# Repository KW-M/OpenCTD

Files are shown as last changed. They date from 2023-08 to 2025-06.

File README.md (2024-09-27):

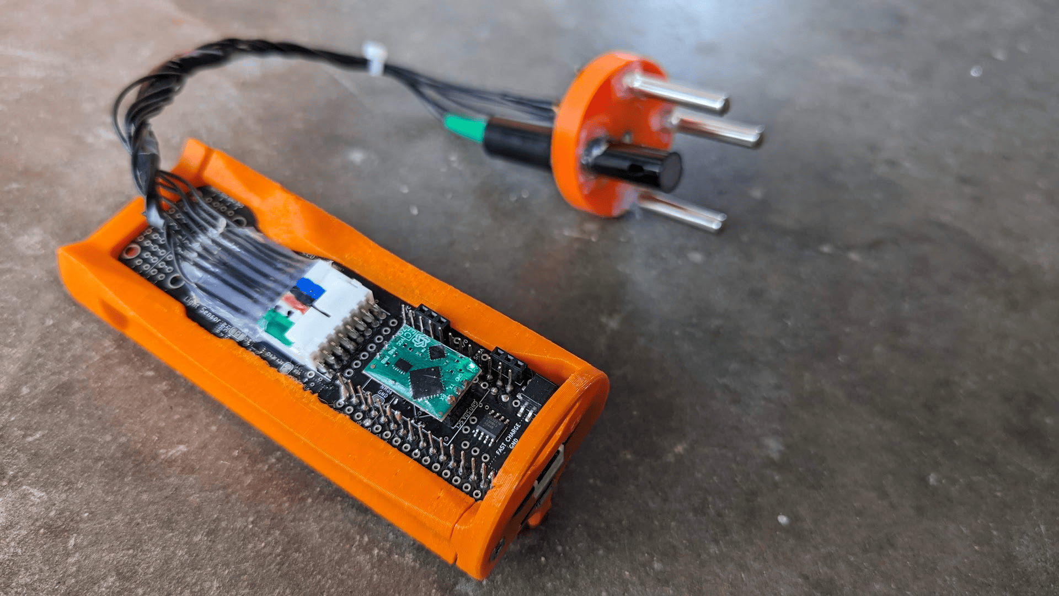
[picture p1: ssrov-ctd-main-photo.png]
SSROV CTD Header Photo


# OpenCTD SSROV / Education Edition!

This fork contains a modified version of the [OpenCTD](https://github.com/OceanographyforEveryone/OpenCTD) designed to be more reliable, easy to use, and useful as a hands-on classroom teaching tool - Developed for the [SSROV Summer Camp](https://ssrovcamp.org/) - Funding provided by the camp and the National Science Foundation

**Improvements**

- Much more reliable magnetic switch - hold to power on/off - works while fully sealed!
- Data download, calibration & configuration over USB - removes the need to take anything out of the tube or change firmware for use & calibration.
- Supports realtime plotting of sensors via the Arduino serial plotter.
- Configurable sample rate for fast response or extended battery life.
- Bright status LEDs that work in sunlight
- Includes proto space for extending with your own sensors or components.
- Built in slots for ambient lux and 9-axis orientation sensors.
- Connectors make major conmponents, mainboard and tube easily replaceable.
- Factory assembly PCB design - less soldering required and better components for very resonable prices via JLCPCB (30$ + shipping for 5 assembled boards).

**There are many other great open source CTDs used for different applications**

CTDizzle: https://github.com/IanTBlack/CTDizzle

Arduino-based Sonde: https://github.com/glockridge/DrifterApplication

OpenCTD: https://github.com/OceanographyforEveryone/OpenCTD

PiCTD: https://github.com/haanhouse/pictd

## Make your own

> Build and ordering guides comming soon

All things related to the SSROV OpenCTD are found in the [SSROV CTD](./SSROV%20CTD/) folder including:

- [Source code](./SSROV%20CTD/Software/Firmware/ssrov_ctd_code) in Arduino c++ and [pre-compiled binaries](./SSROV%20CTD/Software/Firmware/ssrov_ctd_code/build) for the Adafruit Feather Adalogger - M0 microcontroller.
- [PCB designs](./SSROV%20CTD/Hardware/Electronics/PCB/ssrov-kicad-openctd) in KiCad and exported [pcb trace & assembly files](./SSROV%20CTD/Hardware/Electronics/PCB/ssrov-kicad-openctd/production/) for ordering assembled circuit boards from JLCPCB.
- [3D Printer files](./SSROV%20CTD/Hardware/3D-Prints) and [CAD Designs](https://cad.onshape.com/documents/1210ba157fe929ee8ac86200/w/c68b7dc340291ef5042e473d/e/f126e805a19383355f9e1651) for Onshape.

Submit a github issue and let us know if you want make one or modify for your usecase! - We are happy to help!

### Development Notes:

> Please be advised that the rubber o-rings in the yellow Cherne brand endcaps is much stiffer than the rubber used in other endcap brands and has been found to fail consistently in cold water. We do not recommend using Cherne endcaps in your CTD build.
>
> Some batteries ordered from Amazon have the positive and negative termninal reversed. Please check battery polarity before attempting to power your CTD.

# OpenCTD: Oceanography for Everyone

**BELOW IS THE README FROM THE ORIGNAL OPENCTD PROJECT**

- Directions here do not nessisarily apply to ssrov CTD.

The [OpenCTD Construction and
Operation](https://github.com/OceanographyforEveryone/OpenCTD/tree/main/Documentation/Manual)
manual provides a comprehensive, step-by-step guide to building your own
OpenCTD, with a standard construction pathway as well as numerous alternatives
depending on parts availability and technical skills.

The OpenCTD [core software](https://github.com/OceanographyforEveryone/OpenCTD/tree/main/Software) is designed
to be used with an M0-style Arduino microcontroller, for which we recommend the
[Adafruit Adalogger Feather M0](https://www.adafruit.com/product/2796).

---

There is something radical about making and using your own scientific
instruments. The structure of scientific inquiry has coalesced around a model
that is, in general, both expensive and exclusive. This centralizes knowledge
production within a small circle of individuals, organizations, and
institutions who have access to substantial financial resources. This circle
rarely reflects the breadth of identities, experiences, and ways of knowing
that are most directly connected to the places being explored.

By building your own instruments to study and understand the natural world, you
are expanding the circle of knowledge production. A scientist who can make
their own instruments is not beholden to the cycles of funding and access that
constrain formal, institutional inquiry. A researcher who can build and repair
their own equipment is not dependent on the whims of academic sentiment to
decide what is and is not worthy of study. A community leader who has the tools
to create their own data does not have to wait for institutions to take notice
of an emerging crisis before taking action.

The OpenCTD

**You don’t need to ask for permission to understand your world.**

Nowhere is this inequality of access more pronounced than in the ocean
sciences, where all but a few entities have the capital to mount major
oceanographic research campaigns. Even localized coastal research can be
thwarted by lack of access to vessels, equipment, and instruments. As the need
to understand the dramatic changes at the surface and beneath the waves
accelerates, baring the participation of ocean stakeholders erodes our
power to understand, anticipate, and mitigate those changes.

The ocean belongs to everyone. The tools to study the ocean should be
accessible to anyone with the curiosity and motivation to pursue that inquiry.
Chief among these tools is the workhorse of oceanography, the CTD, an
instrument that measures salinity, temperature, and depth. By these
characteristics, scientists can begin to unlock ocean patterns hidden beneath
the sea's surface.

CTDs come in a variety of shapes, sizes, and applications. Most oceanographic
research vessels have a CTD connected to a rosette platform, which houses other
instruments and collects water samples in parallel with real-time data. CTDs
are also commonly attached to fixed moorings, autonomous underwater vehicles
(AUVs), remote-operated vehicles (ROVs), and even to marine animals.

Unfortunately, commercial CTDs are expensive. The most affordable models cost
several thousand dollars. For near-shore oceanographic research on the
relatively shallow continental shelf, this cost can be prohibitive. This
effectively excludes formal researchers from low and middle income countries,
and small island states. Even in high-income countries, formal researchers at
teaching institutions or at early career stages may also find themselves priced
out of ocean research. Informal researchers such as citizen oceanographers,
educators, conservation and management practitioners and students of all levels
face severe challenges accessing expensive scientific instruments.

### Build Your Own CTD

The OpenCTD is a low-cost, open-source CTD designed for budget-restricted
scientists, educators, and researchers working in nearshore coastal ecosystems.
In these waterways, entire research projects can be conducted for less than the
cost of a commercial CTD. OpenCTD was developed by a core team of marine
ecologists in collaboration with a community of scientists, engineers, makers,
and conservation practitioners from around the world. It is assembled from
components commonly available at large hardware stores or through major online
retailers. An Arduino-based microcontroller controls an array of sensors sealed
within a PVC pipe. Power is provided by a standard 3.7V lithium polymer battery
and data are stored in a tab-delimited text file accessed via SD card. All
OpenCTD software is released open source with no restrictions on use.

The OpenCTD is designed to be built by the end-user, providing both access to
the tools of oceanography as well as the skills to maintain, repair, and
replace OpenCTDs. For scientists working in remote settings, the repairability
of the OpenCTD is intended to prevent equipment failures from spiraling into
project failures. For educators seeking novel, in-depth, hands-on STEM
experience for advanced students, the process of building an OpenCTD offers an
introduction to coding, 3D-printing, hardware prototyping, and electronics.
Construction of an OpenCTD can provide a practical foundation for courses in
oceanography and marine or environmental science.

### Core Resources

The [OpenCTD Construction and
Operation](https://github.com/OceanographyforEveryone/OpenCTD/tree/main/Documentation/Manual)
manual provides a comprehensive, step-by-step guide to building your own
OpenCTD, with a standard construction pathway as well as numerous alternatives
depending on parts availability and technical skills. A shorter manual covering just the calibration process is also available.

The OpenCTD [core software](https://github.com/OceanographyforEveryone/OpenCTD/tree/main/Software) is designed
to be used with an M0-style Arduino microcontroller, for which we recommend the
[Adafruit Adalogger Feather M0](https://www.adafruit.com/product/2796).

You can find all the Arduino libraries as described in the manual, as well as
software for calibrating the conductivity sensors in
[Support](https://github.com/OceanographyforEveryone/OpenCTD/tree/main/Software/Support).

Hardware file for both 3D printable components and the control unit PBC can be found in [Hardware](https://github.com/OceanographyforEveryone/OpenCTD/tree/main/Hardware)

**Updated 8/27/2024**

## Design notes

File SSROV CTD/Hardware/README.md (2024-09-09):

# OpenCTD Hardware

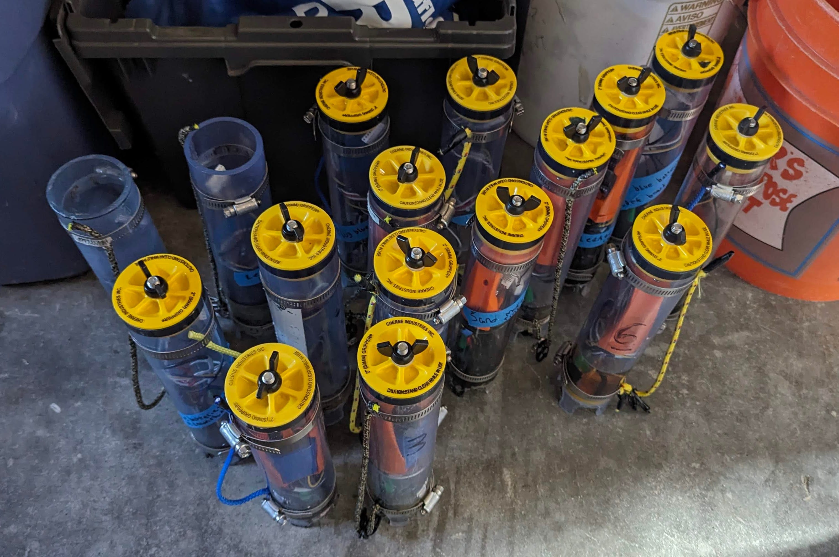
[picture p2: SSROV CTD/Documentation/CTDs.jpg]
SSROV CTDs Assembled

This directory contains files for building the OpenCTD. There are two general systems here:

- The "main board" electronics assembly including microcontroller, sd card, sensor interfaces, power controls, 3D printed internal frame, etc...
- The enclosure, which includes both the clear PVC tube + 3D printed
  base needed to construct the waterproof housing and the epoxied sensors + wires + connector that makes the OpenCTD an oceanographic instrument.

### Electronics

Electronics with tube components attached
The SSROV OpenCTD is controlled by an [Adalogger Feather
M0](https://www.adafruit.com/product/2796) microcontroller development board.
Instructions on how to upload OpenCTD firmware to the microcontroller board can
be found in the [Documentation](../Documentation). General instructions and
learning resources about the Adalogger Feather M0 board itself can be found in
the [Adafruit Learning
Guide](https://learn.adafruit.com/adafruit-feather-m0-adalogger/).

The SSROV OpenCTD mainboard is made from a largely pre-assembled custom pcb. The custom PCB is designed using [KiCad](https://www.kicad.org/), and can
be ordered in small batches from JLCPCB
using the files located in the [PCB](Electronics/PCB) directory.

### Enclosure

Most of the OpenCTD enclosure is constructed from PCV tubing and plumbing components. The base should be 3d printed and permanently epoxied along with the sensors for pressure, temprerature and salinity into the enclosure tube.

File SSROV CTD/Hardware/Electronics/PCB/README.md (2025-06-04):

# OpenCTD SSROV PCB

The OpenCTD main board is designed using [KiCad](https://www.kicad.org/) and made to be fabricated and assembled using JLCPCB.

prebuilt gerber and assembly files can be found in [./ssrov-kicad-openctd/production/](./ssrov-kicad-openctd/production/)
video guide on ordering will be shared soon

Factory Assembled main board:
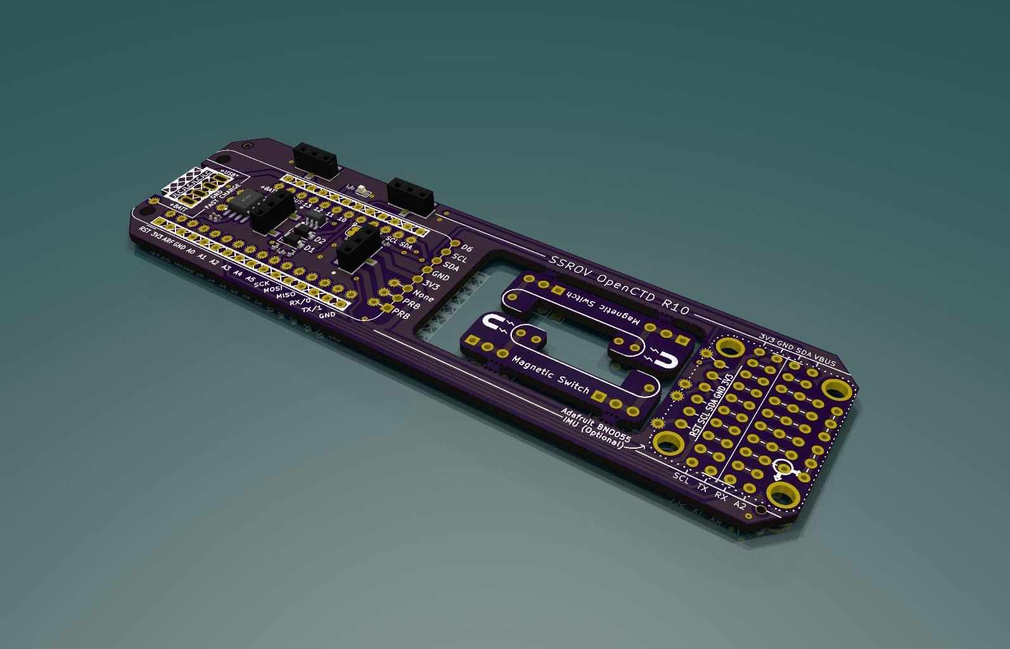
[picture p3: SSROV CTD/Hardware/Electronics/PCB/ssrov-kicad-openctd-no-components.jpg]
Factory Assembled PCB


Main board after manual assembly including optional components:
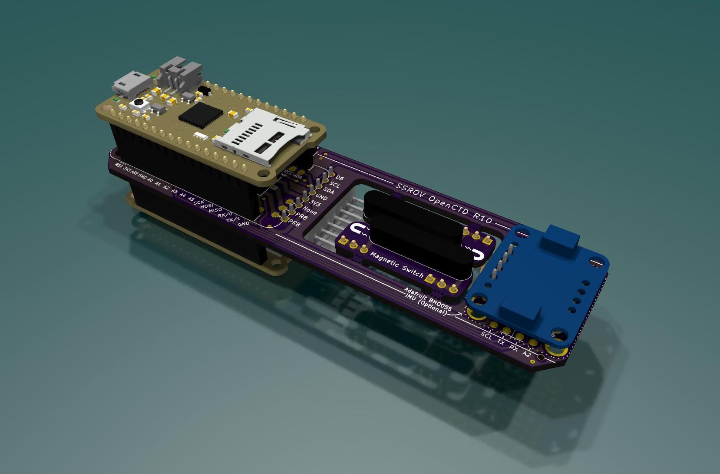
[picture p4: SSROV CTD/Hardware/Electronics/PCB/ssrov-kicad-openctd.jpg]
finished PCB after manual assembly


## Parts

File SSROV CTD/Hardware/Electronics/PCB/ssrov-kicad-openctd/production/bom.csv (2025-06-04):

Designator | Footprint | Quantity | Value | LCSC Part #
C1, C7 | 0402 | 2 | 100nF | C1525
C2, C8 | 0402 | 2 | 10uF | C15525
D1, D2 | D_SOD-123 | 2 | 1N4148W | C81598
D6-R4 | 0402 | 1 | 4.7k | C25900
EC_CONN_A1, EC_CONN_B5, REED_SWITCH_CONN1, REED_SWITCH_CONN2 | HDR-SMD_3P-P2.54-V-M-LS4.8_R1 | 4 | Conn_01x03_Female | C42379196
LED-R3 | 0402 | 1 | 470Ω | C25117
LED_D3 | 0603 | 1 | WHITE LED | C2290
NOT-NOT-GATE1 | SOT-23-6_L2.9-W1.6-P0.95-LS2.8-BL | 1 | SN74LVC2G14DBVR | C12401
PWR-R1, SCL-R5, SDA-R6 | 0402 | 3 | 10k | C25744
PWR-R2, PWR-R3 | 0402 | 2 | 20k | C25765
U2 | SOIC-8_L4.9-W3.9-P1.27-LS6.0-BL | 1 | DS3231MZ+ | C107410

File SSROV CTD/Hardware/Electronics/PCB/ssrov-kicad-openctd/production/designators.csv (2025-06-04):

BNO055_IMU1:1
C1:1
C2:1
C7:1
C8:1
D1:1
D2:1
D6-R4:1
EC_CONN_A1:1
EC_CONN_B5:1
FASTCHARGE_CONN1:1
J1:1
J3:1
JB1:1
JB3:1
JP1:1
JP6:1
JP7:1
LED-R3:1
LED_D3:1
MOUSE-BITE-2MM-SLOT:4
NOT-NOT-GATE1:1
OSHW_LOGO:1
PERMA_BREADBOARD_AREA1:1
PWR-R1:1
PWR-R2:1
PWR-R3:1
REED_SWITCH1:1
REED_SWITCHB1:1
REED_SWITCH_CONN1:1
REED_SWITCH_CONN2:1
REF**:2
SCL-R5:1
SDA-R6:1
TOP_HOLE1:2
TP1:1
TP10:1
TP11:1
TP12:1
TP13:1
TP14:1
TP15:1
TP2:1
TP21:1
TP22:1
TP23:1
TP24:1
TP25:1
TP26:1
TP27:1
TP28:1
TP29:1
TP3:1
TP30:1
TP31:1
TP32:1
TP33:1
TP34:1
TP35:1
TP36:1
TP37:1
TP38:1
TP39:1
TP4:1
TP40:1
TP42:1
TP43:1
TP44:1
TP46:1
TP5:1
TP6:1
TP7:1
TP8:1
TP9:1
TUBE_CONNECTIONS1:1
U1:1
U2:1
U3:1

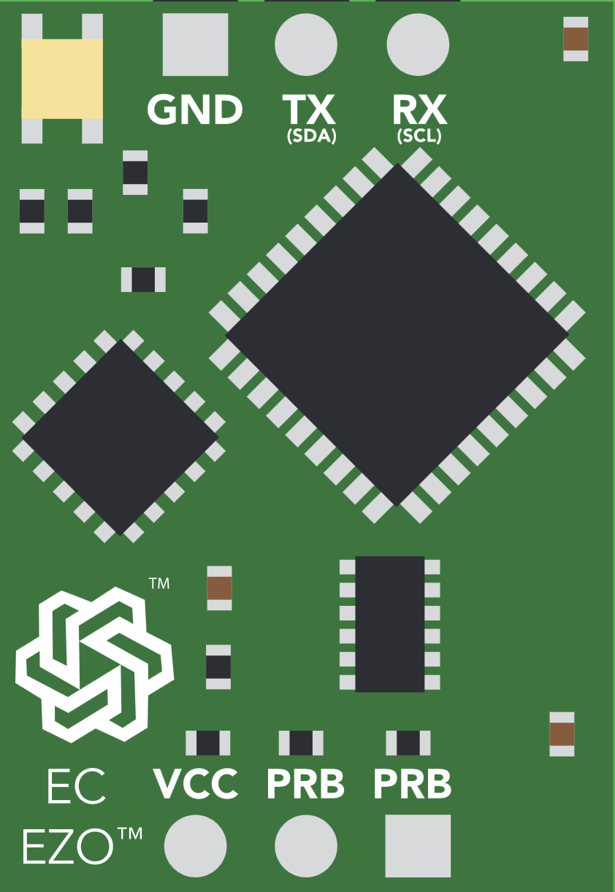
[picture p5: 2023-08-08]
SSROV CTD/Hardware/Electronics/PCB/ssrov-kicad-openctd/components/EZO_EC_Chip/Screenshot 2023-04-22 at 8.32.12 PM.png

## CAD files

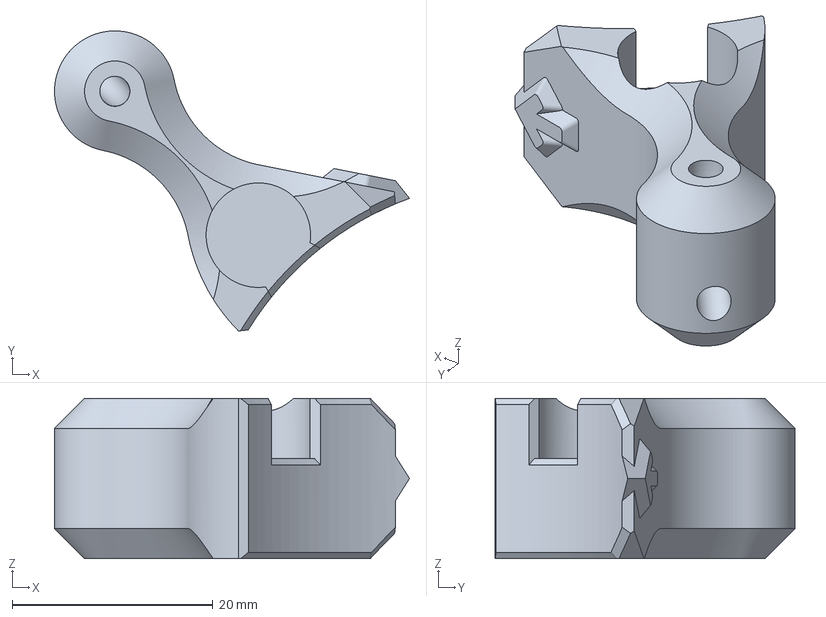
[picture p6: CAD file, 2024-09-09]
SSROV CTD/Hardware/3D-Prints/Mag Switch Tool.3mf
35.4 x 29.9 x 16.0 mm

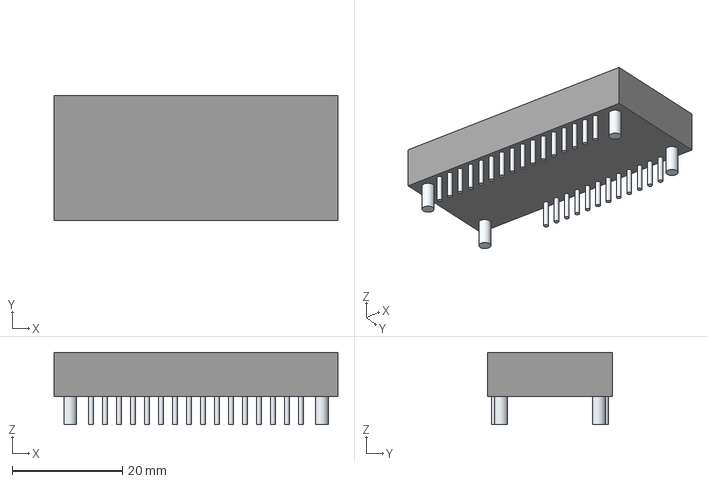
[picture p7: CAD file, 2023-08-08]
SSROV CTD/Hardware/Electronics/PCB/ssrov-kicad-openctd/components/2795 Feather 32u4 Adalogger/2796.stp
51.6 x 22.8 x 13.1 mm
Leads x 32

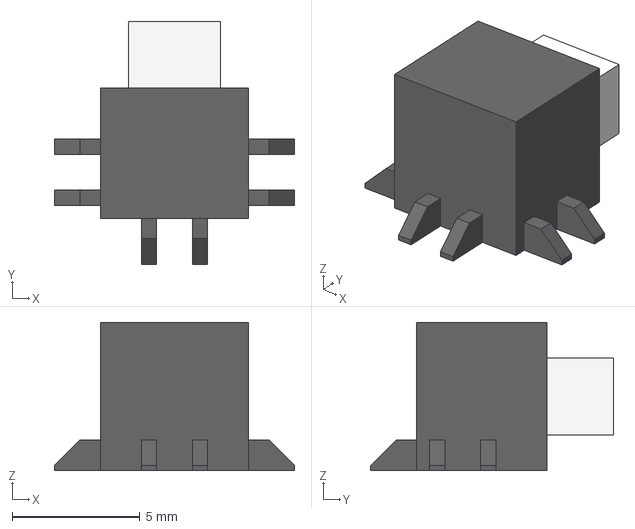
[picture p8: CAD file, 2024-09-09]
SSROV CTD/Hardware/Electronics/PCB/ssrov-kicad-openctd/components/3D Models/Push_button_XKB5858-W-F-75 - Part 1.step
9.40 x 9.50 x 5.80 mm

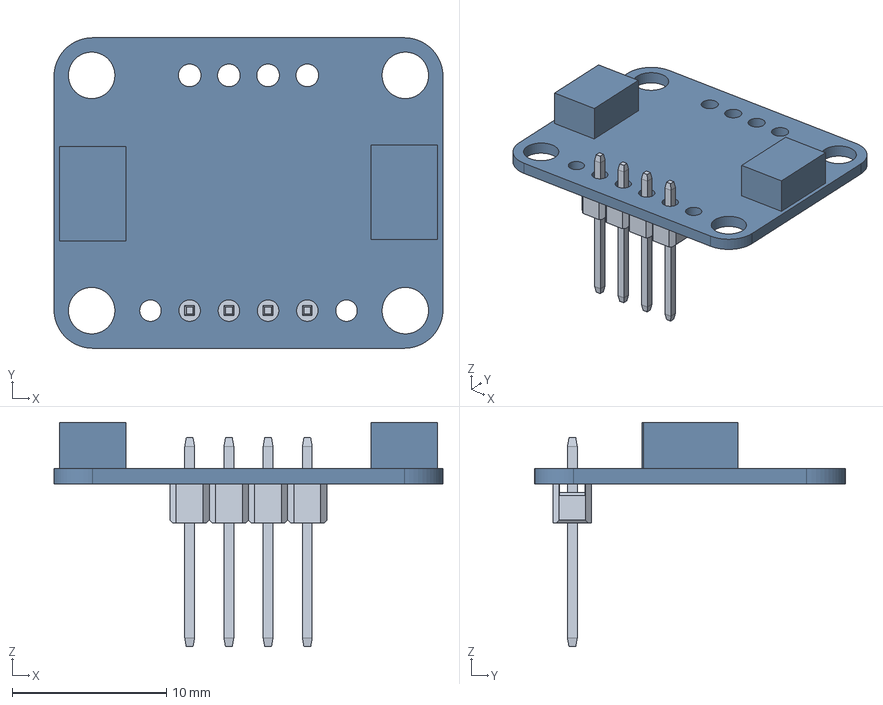
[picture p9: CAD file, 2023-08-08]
SSROV CTD/Hardware/Electronics/PCB/ssrov-kicad-openctd/components/Adafruit BNO055 IMU Fusion/Adafruit BNO055 IMU Fusion W Pins.step
25.2 x 20.1 x 14.5 mm
Adafruit BNO055 IMU Fusion
1x4 Male Pin Header x 5

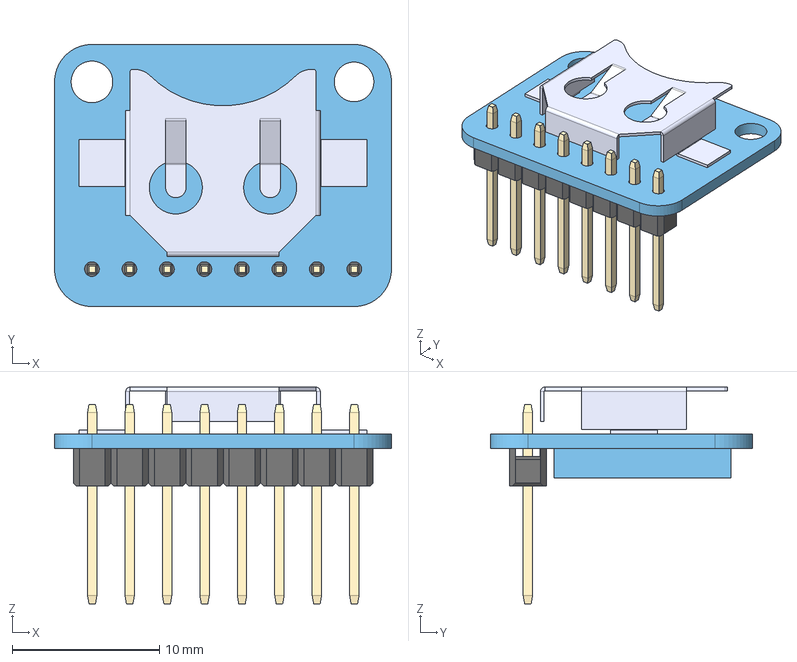
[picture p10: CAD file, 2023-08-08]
SSROV CTD/Hardware/Electronics/PCB/ssrov-kicad-openctd/components/Adafruit RTC Breakout - 3013/Adafruit_RTC_Breakout_3013.step
22.9 x 17.8 x 14.7 mm
1x4 Male Pin Header x 2
BK-885--3DModel-STEP-1

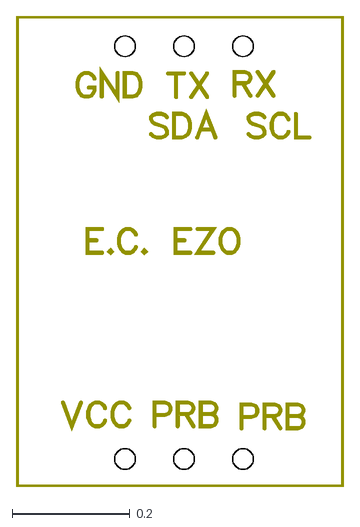
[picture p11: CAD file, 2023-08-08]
SSROV CTD/Hardware/Electronics/PCB/ssrov-kicad-openctd/components/EZO_EC_Chip/EC-EZO-LAYOUT.dxf
0.555 x 0.798

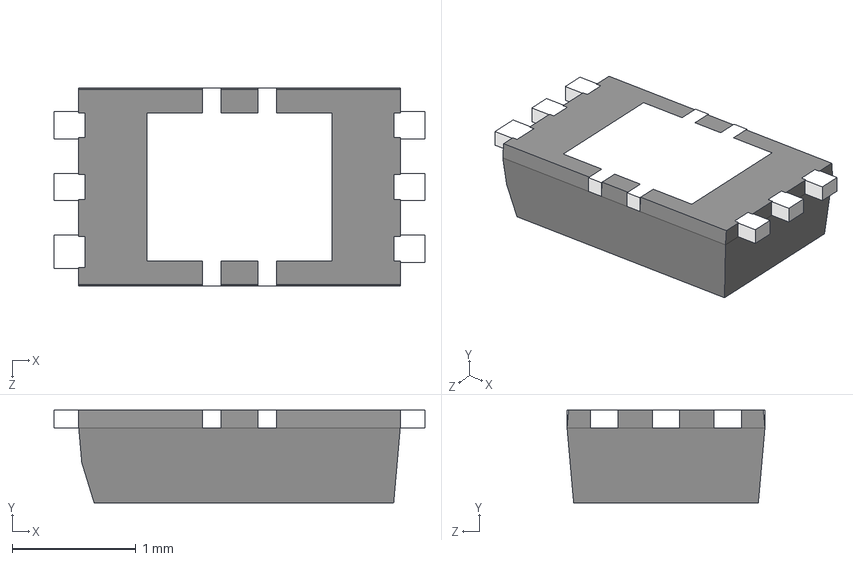
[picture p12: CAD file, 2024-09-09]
SSROV CTD/Hardware/Electronics/PCB/ssrov-kicad-openctd/components/LIB_BH1750FVI-TR/BH1750FVI-TR/3D/BH1750FVI-TR.stp
3.00 x 0.75 x 1.60 mm

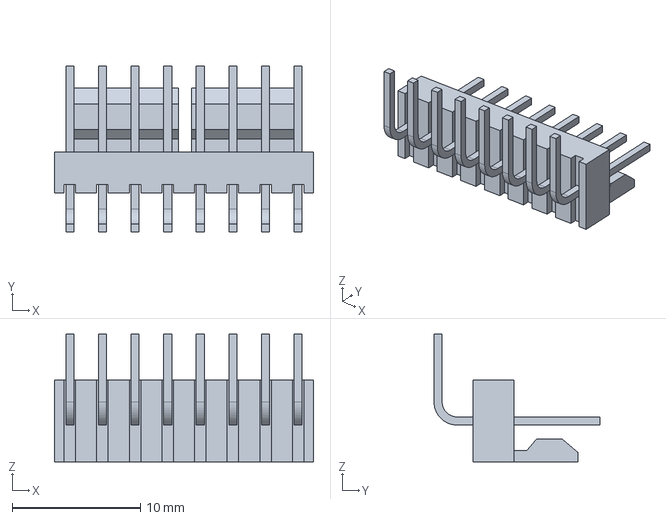
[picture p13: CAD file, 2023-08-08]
SSROV CTD/Hardware/Electronics/PCB/ssrov-kicad-openctd/components/Molex Male 22-05-3081 Connector/22-05-3081.stp
20.2 x 12.9 x 9.93 mm

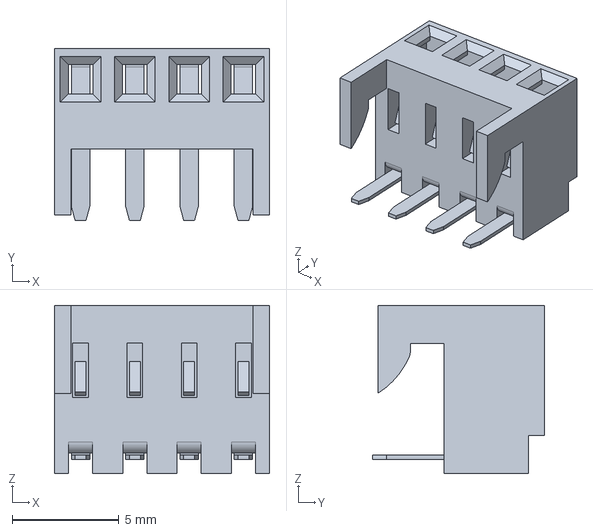
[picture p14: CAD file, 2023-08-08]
SSROV CTD/Hardware/Electronics/PCB/ssrov-kicad-openctd/components/MOLEX_22-16-2041/3D/22-16-2041.stp
10.1 x 8.05 x 7.87 mm

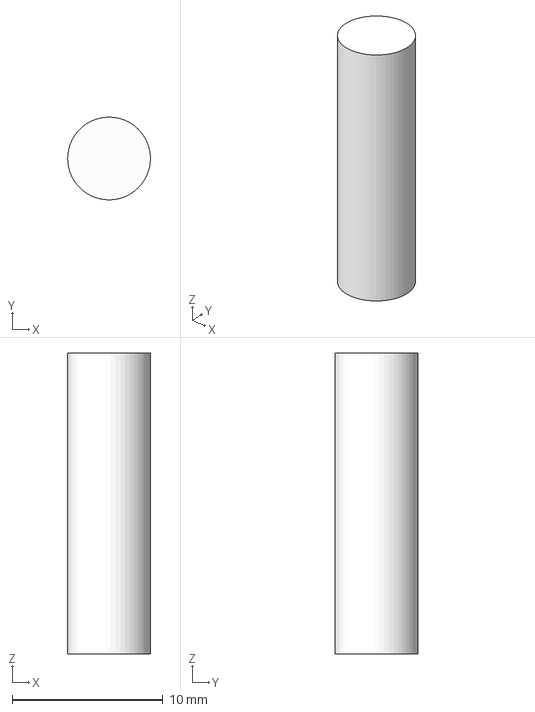
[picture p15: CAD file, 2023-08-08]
SSROV CTD/Hardware/Electronics/PCB/ssrov-kicad-openctd/components/TSL25911FN/3D/Light Sensor View Region.step
5.49 x 5.50 x 20.0 mm

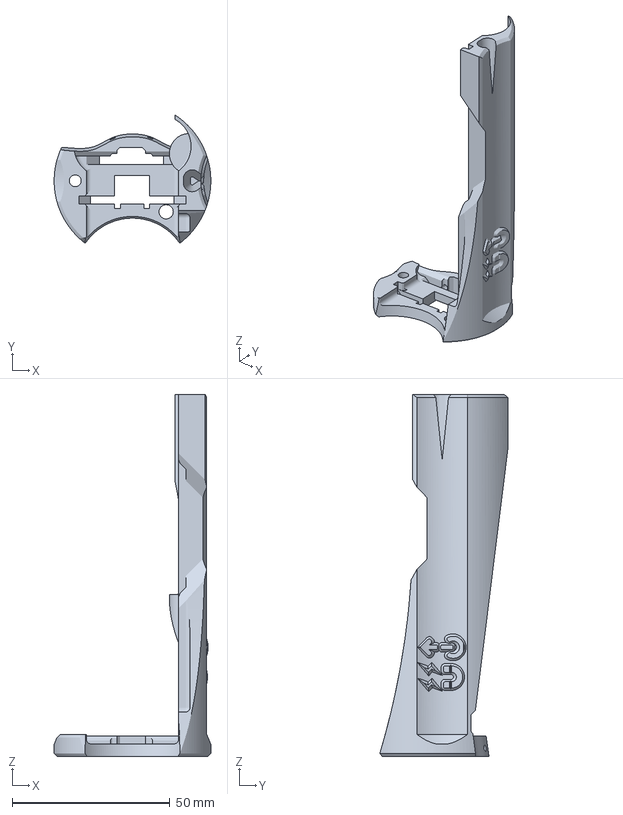
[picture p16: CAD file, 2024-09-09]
SSROV CTD/Hardware/3D-Prints/CTD Chassis Part A.3mf
49.7 x 40.7 x 114.8 mm

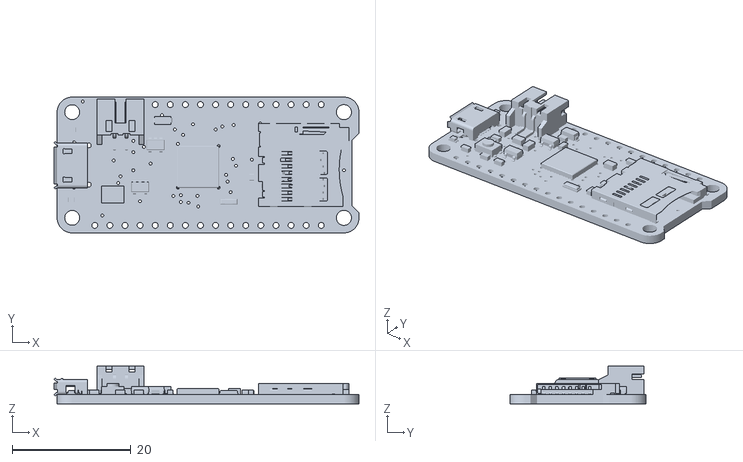
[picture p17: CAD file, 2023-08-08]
SSROV CTD/Hardware/Electronics/PCB/ssrov-kicad-openctd/components/2795 Feather 32u4 Adalogger/2795 Feather 32u4 Adalogger.stl
51.3 x 22.9 x 6.37

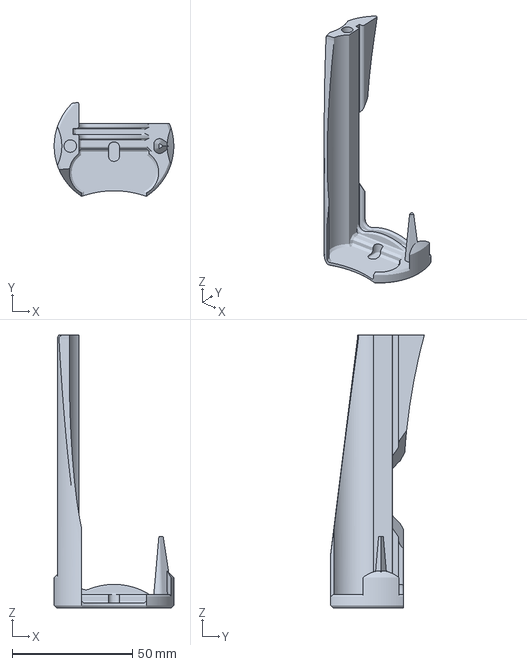
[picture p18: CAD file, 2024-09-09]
SSROV CTD/Hardware/3D-Prints/CTD Chassis Part B.3mf
49.7 x 39.0 x 113.4 mm

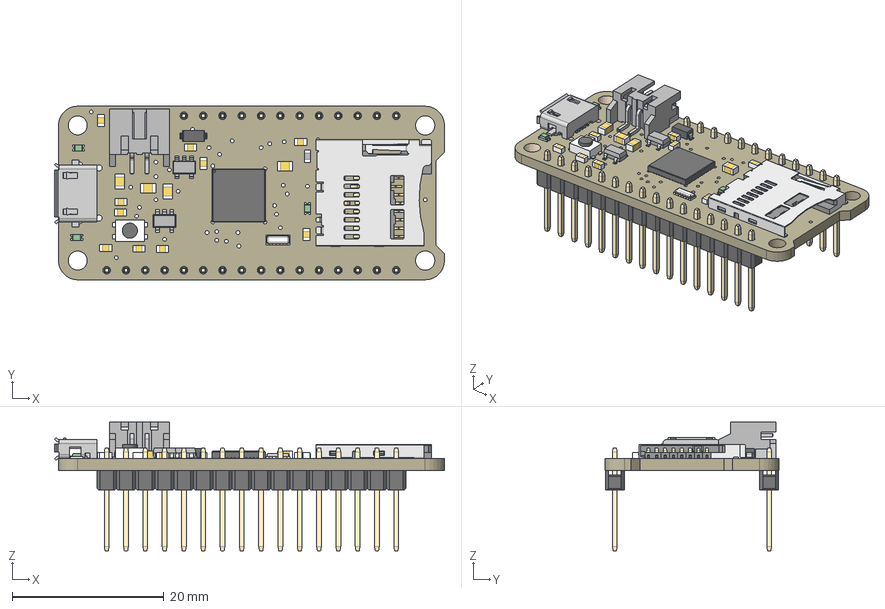
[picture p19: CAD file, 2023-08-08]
SSROV CTD/Hardware/Electronics/PCB/ssrov-kicad-openctd/components/2795 Feather 32u4 Adalogger/2795 Feather 32u4 Adalogger with pins.step
51.3 x 22.9 x 16.9 mm
Board
10µF x 4
100k x 10
GREEN x 3
ATMEGA32U4-MU
SPST_TACT-KMR2
8MHz
microUSB
MCP73831T-2ACI/OT x 2
MBR120
JSTPH
microsd
100K_1
1x4 Male Pin Header x 7

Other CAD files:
SSROV CTD/Hardware/3D-Prints/OpenCTD_M0_Baseplate_SparkfunBreakout.3mf
SSROV CTD/Hardware/3D-Prints/OpenCTD_M0_Baseplate_OpenROV_IMU.3mf
SSROV CTD/Hardware/3D-Prints/2-inch_PVC_PaintCap_Bottom.stl
SSROV CTD/Hardware/3D-Prints/OpenCTD_M0_Baseplate.3mf

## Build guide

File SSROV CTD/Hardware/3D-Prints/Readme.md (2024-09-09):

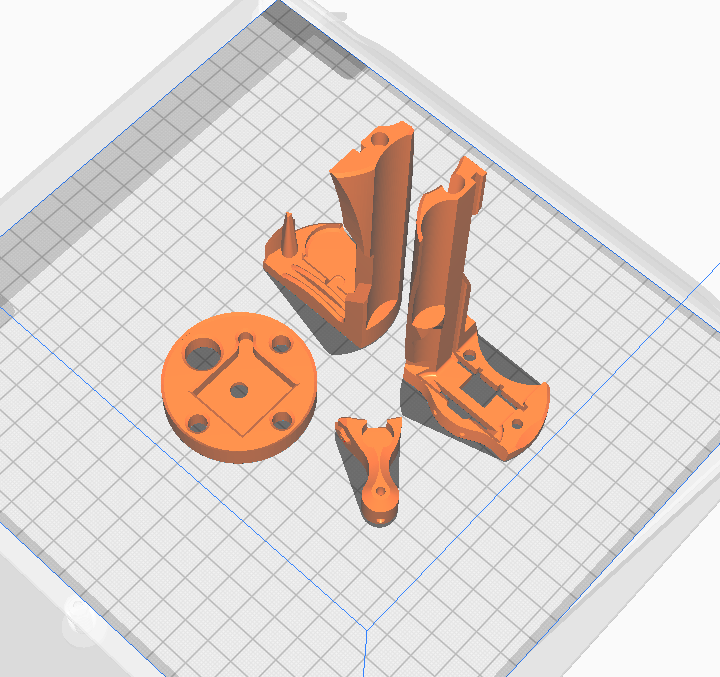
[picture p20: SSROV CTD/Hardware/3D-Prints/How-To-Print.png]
How to setup models for printing


## 3D Printing the SSROV OpenCTD

Everything can be printed WITHOUT SUPPORTS if layed flat and vetical as shown in the photo above.

Print all of these files:

- [CTD Chassis Part A.3mf](<CTD Chassis Part A.3mf>)
- [CTD Chassis Part B.3mf](<CTD Chassis Part B.3mf>)
- [Mag Switch Tool.3mf](<Mag Switch Tool.3mf>)

Plus print one base plate based on which kind of pressure sensor you have:

- [OpenCTD_M0_Baseplate_SparkfunBreakout.3mf](./OpenCTD_M0_Baseplate_SparkfunBreakout.3mf) - Recommended base plate for use with Sparkfun 14Bar pressure breakout board as included in the parts list for the SSROV CTD.
- [OpenCTD_M0_Baseplate.3mf](./OpenCTD_M0_Baseplate.3mf) - For use if mounting the 14 bar Pressure sensor and adafruit breakout yourself (see build instructions in main OpenCTD github).
- [OpenCTD_M0_Baseplate_OpenROV_IMU.3mf](./OpenCTD_M0_Baseplate_OpenROV_IMU.3mf) - Not recommended, OpenRov was no longer making these at time of writing.

## Making it your own:

The CAD for the SSROV OpenCTD can be found on [Onshape](https://cad.onshape.com/documents/1210ba157fe929ee8ac86200/w/c68b7dc340291ef5042e473d/e/c499e89a301fe88104222f74) and exported in a variety of formats

For best compatibility, make sure to export the entire assembly - as refrences are used between parts.

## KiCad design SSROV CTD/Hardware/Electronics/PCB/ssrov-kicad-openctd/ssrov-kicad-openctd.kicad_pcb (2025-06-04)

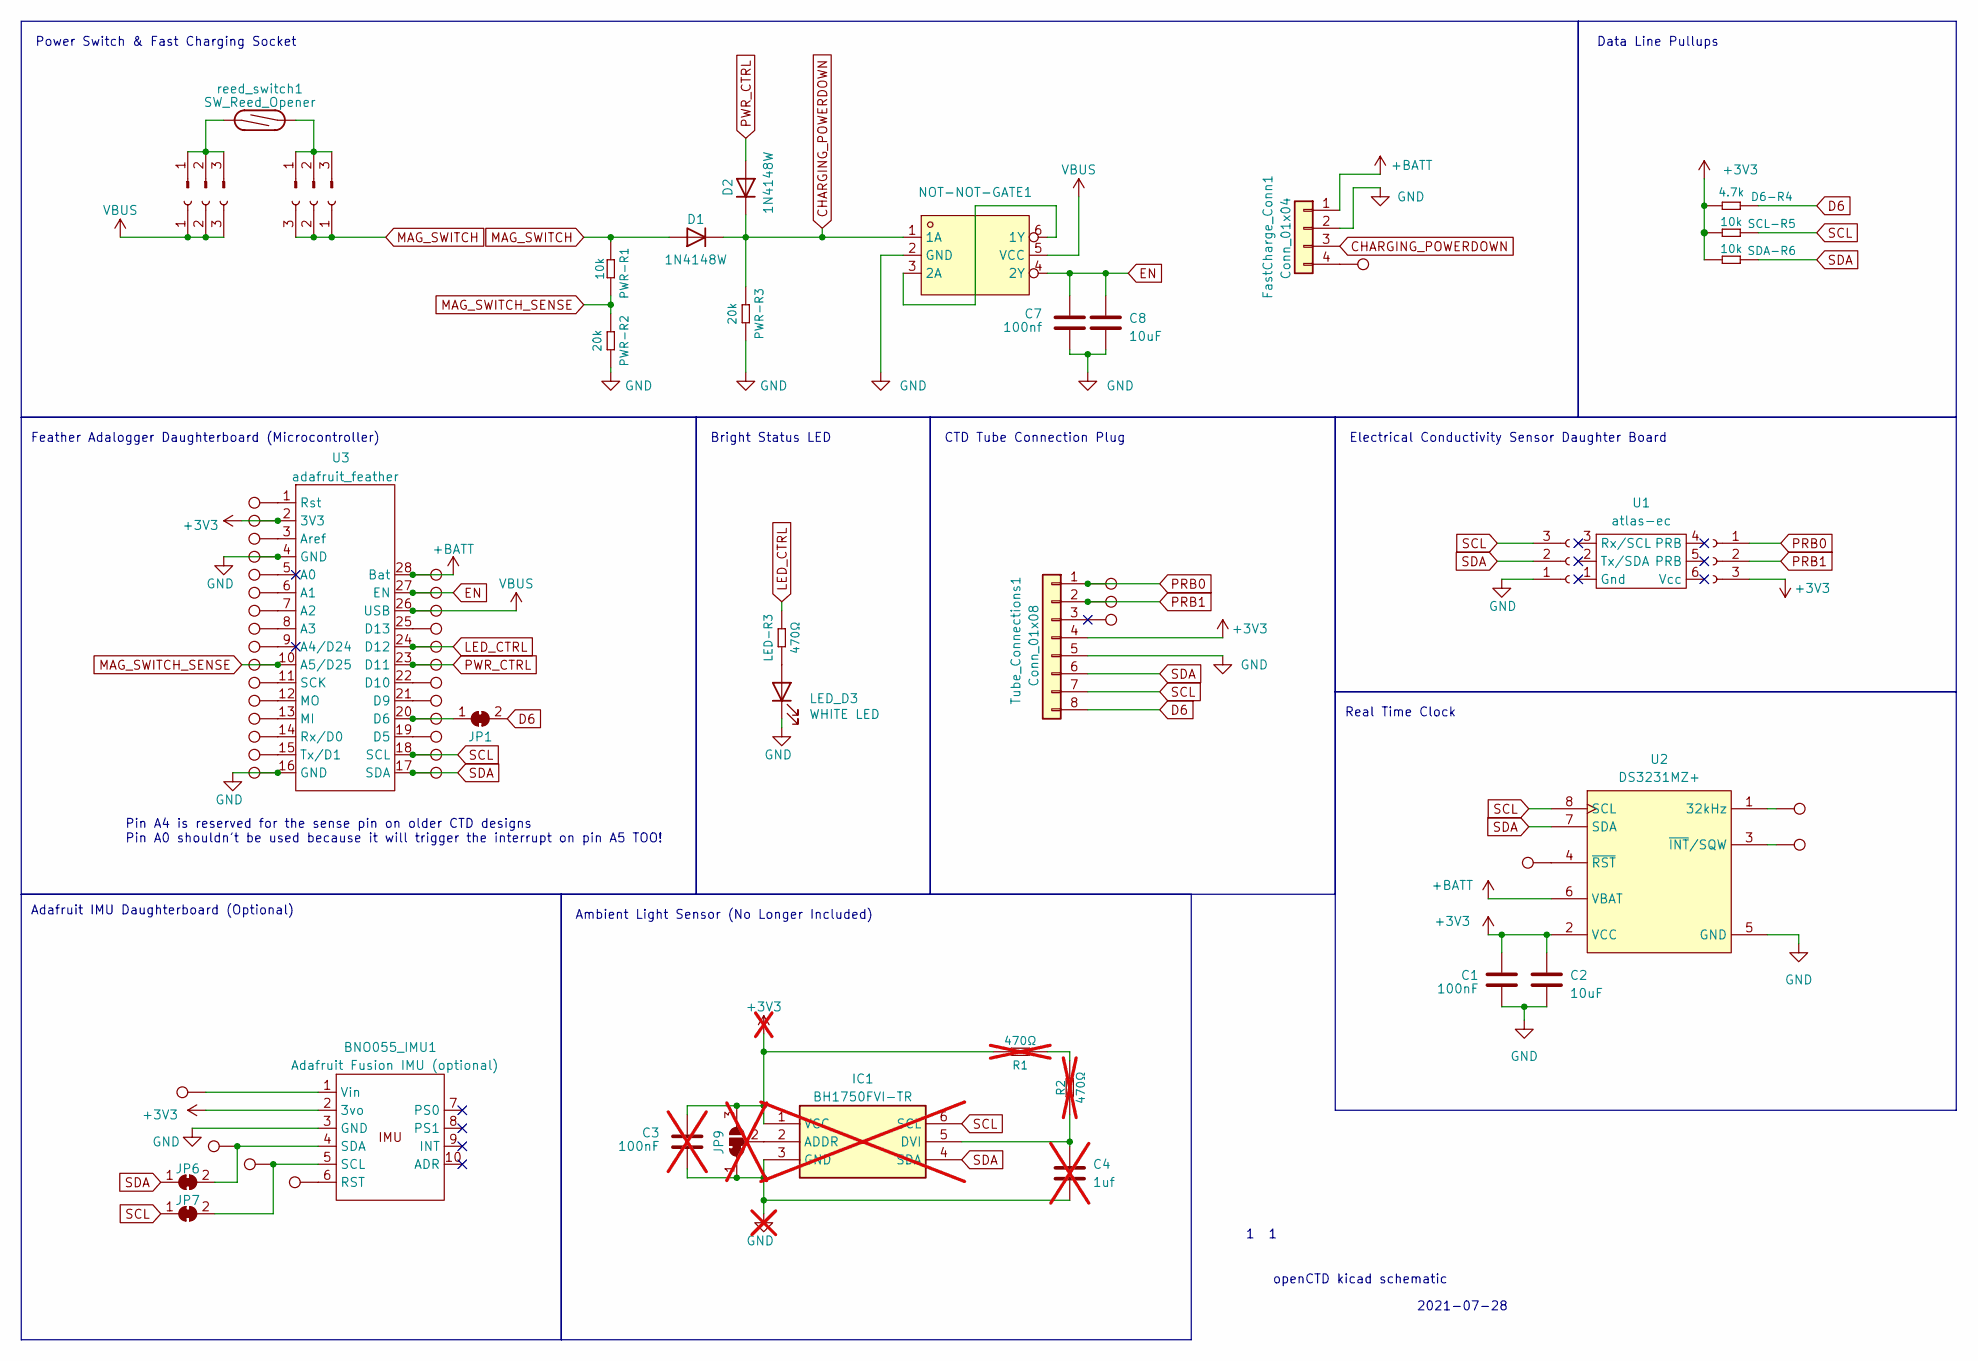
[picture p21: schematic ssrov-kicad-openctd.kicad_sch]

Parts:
BNO055_IMU1: Adafruit Fusion IMU (optional); Adafruit BNO055 IMU fusion breakout board
C1: 100nF; C_0402_1005Metric; LCSC Part C1525
C2, C8: 10uF; C_0402_1005Metric; LCSC Part C15525
C3: 100nF; C_0402_1005Metric; LCSC Part C1525; not fitted
C4: 1uf; C_0402_1005Metric; LCSC Part C52923; not fitted
C7: 100nf; C_0402_1005Metric; LCSC Part C1525
D1, D2: 1N4148W; D_SOD-123; LCSC Part C81598
D6-R4: 4.7k; R_0402_1005Metric; LCSC Part C25900
EC_Conn_A1: Conn_01x03_Female; HDR-SMD_3P-P2.54-V-M-LS4.8_R1; LCSC Part C42379196
EC_Conn_B5: Conn_01x03_Female; HDR-SMD_3P-P2.54-V-M-LS4.8_R1; LCSC Part C42379196
FastCharge_Conn1: Conn_01x04; Molex_KK_Female_Horizontal_PinHeader_1x04
IC1: BH1750FVI-TR; WSOF6; Mouser Part Number 755-BH1750FVI-TR; not fitted
J1, J3: Conn_01x03_Pin; PinHeader_1x03_P2.54mm_Vertical
JP1, JP6, JP7: SolderJumper_2_Bridged; Cuttable_SolderJumper-2_P1.3mm_Bridged_RoundedPad1.0x1.5mm
JP9: SolderJumper_3_Bridged12; SolderJumper-3_P1.3mm_Bridged12_RoundedPad1.0x1.5mm; not fitted
LED-R3: 470Ω; R_0402_1005Metric; LCSC Part C25117
LED_D3: WHITE LED; LED_0603_1608Metric; LCSC Part C2290
NOT-NOT-GATE1: SN74LVC2G14DBVR; SOT-23-6_L2.9-W1.6-P0.95-LS2.8-BL; LCSC Part C12401
PWR-R1: 10k; R_0402_1005Metric; LCSC Part C25744
PWR-R2, PWR-R3: 20k; R_0402_1005Metric; LCSC Part C25765
R1, R2: 470Ω; R_0402_1005Metric; LCSC Part C25117; not fitted
Reed_Switch_Conn1, Reed_Switch_Conn2: Conn_01x03_Female; HDR-SMD_3P-P2.54-V-M-LS4.8_R1; LCSC Part C42379196
SCL-R5: 10k; R_0402_1005Metric; LCSC Part C25744
SDA-R6: 10k; R_0402_1005Metric; LCSC Part C25744
TP1, TP2, TP3, TP4, TP5, TP6, TP7, TP8, TP9, TP10, TP11, TP12, TP13, TP14, TP15, TP21, TP22, TP23, TP24, TP25, TP26, TP27, TP28, TP29, TP30, TP31, TP32, TP33, TP34, TP35, TP36, TP37, TP38, TP39, TP40, TP42, TP43, TP44, TP46: test.point_single_pad_0.8
Tube_Connections1: Conn_01x08; SHDRRA8W62P0X254_1X8_2032X818X660P 22-05-3081
U1: atlas-ec; Atlas_EC_Silkscreen_Only
U2: DS3231MZ+; SOIC-8_L4.9-W3.9-P1.27-LS6.0-BL; LCSC Part C107410
U3: adafruit_feather; Adafruit_Feather_With2MountingHoles
reed_switch1: SW_Reed_Opener; Littelfuse Reed Switch 59050-1-S

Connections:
+3V3: BNO055_IMU1.2 (3vo), C1.2, C2.1, C3.2, D6-R4.1, EC_Conn_B5.3, IC1.1 (VCC), JP9.3 (B), R1.1, SCL-R5.1, SDA-R6.1, TP22.1, Tube_Connections1.4, U2.2 (VCC), U3.2 (3V3); also elsewhere on the board
+BATT: FastCharge_Conn1.1, TP1.1, U2.6 (VBAT), U3.28 (Bat)
CHARGING_POWERDOWN: D1.1 (K), D2.1 (K), FastCharge_Conn1.3, NOT-NOT-GATE1.1 (1A), PWR-R3.2
D6: D6-R4.2, JP1.2 (B), Tube_Connections1.8
EN: C7.2, C8.1, NOT-NOT-GATE1.4 (2Y), TP2.1, U3.27 (EN)
GND: BNO055_IMU1.3 (GND), C1.1, C2.2, C3.1, C4.2, C7.1, C8.2, EC_Conn_A1.1, FastCharge_Conn1.2, IC1.3 (GND), JP9.1 (A), LED_D3.1 (K), NOT-NOT-GATE1.2 (GND), PWR-R2.1, PWR-R3.1, TP24.1, TP36.1, Tube_Connections1.5, U2.5 (GND), U3.4 (GND), U3.16 (GND); also elsewhere on the board
LED_CTRL: LED-R3.1, TP5.1, U3.24 (D12)
MAG_SWITCH: D1.2 (A), PWR-R1.2, Reed_Switch_Conn2.1, Reed_Switch_Conn2.2, Reed_Switch_Conn2.3
MAG_SWITCH_SENSE: PWR-R1.1, PWR-R2.2, TP30.1, U3.10 (A5/D25)
unnamed: BNO055_IMU1.6 (RST), TP42.1
unnamed: BNO055_IMU1.5 (SCL), JP7.2 (B), TP43.1
unnamed: BNO055_IMU1.4 (SDA), JP6.2 (B), TP44.1
unnamed: BNO055_IMU1.1 (Vin), TP40.1
unnamed: C4.1, IC1.5 (DVI), R2.2
unnamed: FastCharge_Conn1.4, TP46.1
unnamed: IC1.2 (ADDR), JP9.2 (C)
unnamed: J1.1, J1.2, J1.3, reed_switch1.2
unnamed: J3.1, J3.2, J3.3, reed_switch1.1
unnamed: JP1.1 (A), TP9.1, U3.20 (D6)
unnamed: LED-R3.2, LED_D3.2 (A)
unnamed: NOT-NOT-GATE1.3 (2A), NOT-NOT-GATE1.6 (1Y)
unnamed: R1.2, R2.1
unnamed: TP39.1, U2.1 (32kHz)
unnamed: TP38.1, U2.3 (~INT/SQW)
unnamed: TP37.1, U2.4 (~RST)
unnamed: TP25.1, U3.5 (A0)
unnamed: TP26.1, U3.6 (A1)
unnamed 45: TP27.1, U3.7 (A2); also elsewhere on the board
unnamed: TP28.1, U3.8 (A3)
unnamed: TP29.1, U3.9 (A4/D24)
unnamed: TP23.1, U3.3 (Aref)
unnamed: TP10.1, U3.19 (D5)
unnamed: TP8.1, U3.21 (D9)
unnamed: TP7.1, U3.22 (D10)
unnamed: TP4.1, U3.25 (D13)
unnamed: TP33.1, U3.13 (MI)
unnamed: TP32.1, U3.12 (MO)
unnamed: TP21.1, U3.1 (Rst)
unnamed 56: TP34.1, U3.14 (Rx/D0); also elsewhere on the board
unnamed: TP31.1, U3.11 (SCK)
unnamed 58: TP35.1, U3.15 (Tx/D1); also elsewhere on the board
PRB0: EC_Conn_B5.1, TP15.1, Tube_Connections1.1
PRB1: EC_Conn_B5.2, TP14.1, Tube_Connections1.2
PWR_CTRL: D2.2 (A), TP6.1, U3.23 (D11)
SCL: EC_Conn_A1.3, IC1.6 (SCL), JP7.1 (A), SCL-R5.2, TP11.1, Tube_Connections1.7, U2.8 (SCL), U3.18 (SCL); also elsewhere on the board
SDA: EC_Conn_A1.2, IC1.4 (SDA), JP6.1 (A), SDA-R6.2, TP12.1, Tube_Connections1.6, U2.7 (SDA), U3.17 (SDA); also elsewhere on the board
VBUS: NOT-NOT-GATE1.5 (VCC), Reed_Switch_Conn1.1, Reed_Switch_Conn1.2, Reed_Switch_Conn1.3, TP3.1, U3.26 (USB); also elsewhere on the board

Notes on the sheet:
Data Line Pullups
Electrical Conductivity Sensor Daughter Board
Bright Status LED
2021-07-28
Real Time Clock
Ambient Light Sensor (No Longer Included)
openCTD kicad schematic
Adafruit IMU Daughterboard (Optional)
Power Switch & Fast Charging Socket
Pin A4 is reserved for the sense pin on older CTD designs Pin A0 shouldn't be used because it will trigger the interrupt on pin A5 TOO!
CTD Tube Connection Plug
Feather Adalogger Daughterboard (Microcontroller)

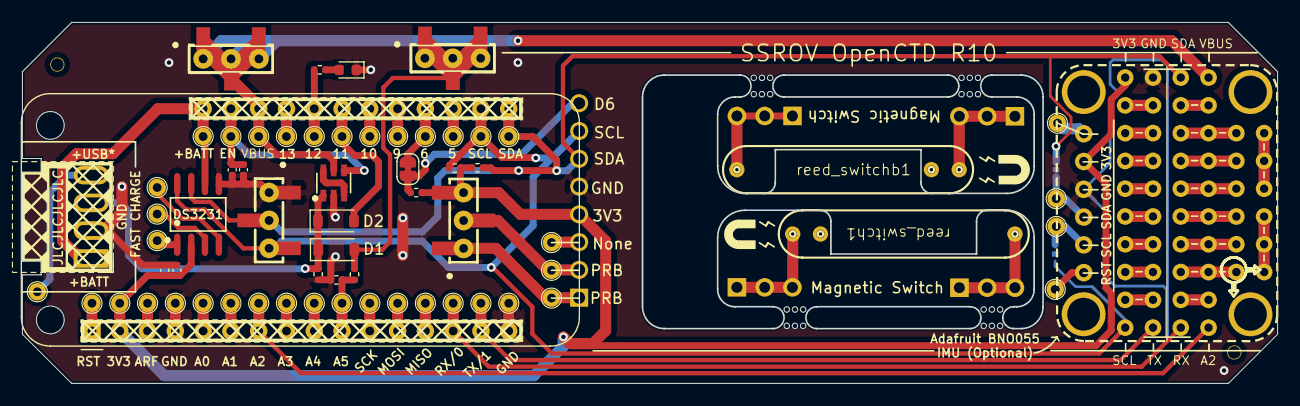
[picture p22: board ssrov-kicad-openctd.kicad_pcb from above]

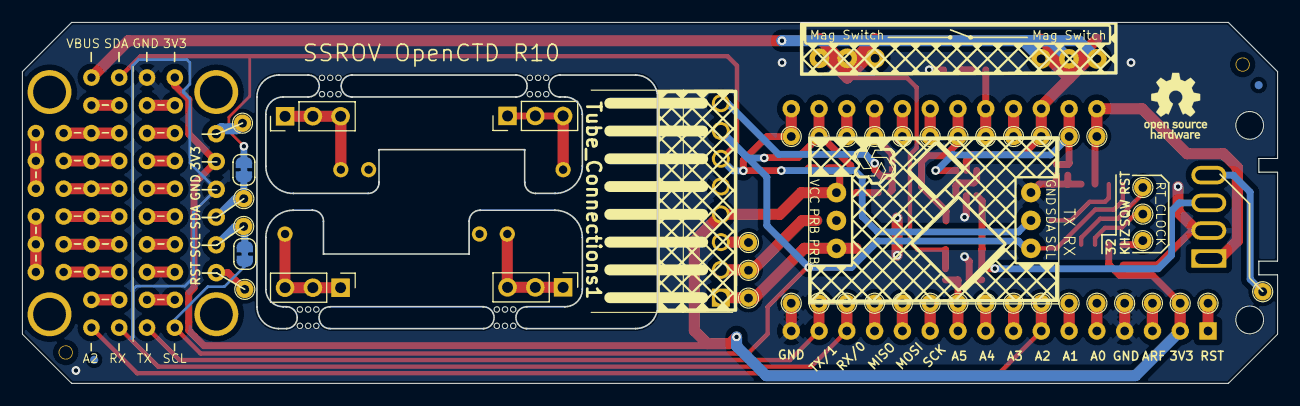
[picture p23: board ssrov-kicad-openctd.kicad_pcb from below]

Board: 2 copper layers, 114.7 x 33.0 mm, 81 parts (9 on the bottom side), 46 nets.

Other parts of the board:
JB1, JB3: Conn_01x03_Pin; PinHeader_1x03_P2.54mm_Vertical
OSHW_Logo: OSHW-Logo_5.7x6mm_SilkScreen
Perma_Breadboard_Area1: PermaProto_Breadboard_Area
mouse-bite-2mm-slot, mouse-bite-2mm-slot#2, mouse-bite-2mm-slot#3, mouse-bite-2mm-slot#4: VAL**; mouse-bite-2mm-slot
reed_switchb1: SW_Reed_Opener; Littelfuse Reed Switch 59050-1-S
top_hole1, top_hole1#2: JLCPCBA_mount_hole

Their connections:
+3V3: Perma_Breadboard_Area1.2; also elsewhere on the board
GND: Perma_Breadboard_Area1.3; also elsewhere on the board
unnamed 45: Perma_Breadboard_Area1.38; also elsewhere on the board
unnamed 56: Perma_Breadboard_Area1.37; also elsewhere on the board
unnamed 58: Perma_Breadboard_Area1.36; also elsewhere on the board
Reed_switch_b1: JB1.1, JB1.2, JB1.3, reed_switchb1.2
Reed_switch_b3: JB3.1, JB3.2, JB3.3, reed_switchb1.1
SCL: Perma_Breadboard_Area1.34; also elsewhere on the board
SDA: Perma_Breadboard_Area1.36; also elsewhere on the board
VBUS: Perma_Breadboard_Area1.39; also elsewhere on the board

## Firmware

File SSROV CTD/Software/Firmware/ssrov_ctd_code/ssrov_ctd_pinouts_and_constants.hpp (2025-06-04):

#include "Adafruit_USBD_CDC.h"
/**************************************************************/
/** This file contains Board & Circut Specific Constants & ***/
/** Pinouts (edit if needed) ********************************/
/***********************************************************/

#ifndef SSROV_CTD_PINOUTS_AND_CONSTANTS_H_
#define SSROV_CTD_PINOUTS_AND_CONSTANTS_H_

#define TRUE 1
#define FALSE 0

/* ------------------------------------*/
/* ------ Indicator Lights -----------*/
/* ----------------------------------*/

#define LED_STAT1 LED_BUILTIN  // Indicator light 1 (Red, near plug, Soldered onto feather board).
#define LED_STAT2 12           // bright white LED on PCB.
#define LED_STAT3 8            // green led on feather board

/* -----------------------------------*/
/* ------ Real Time Clock -----------*/
/* ---------------------------------*/

#include "RTClib.h"   // does fit in feather m0 memory
#define RTC_TYPE 'D'  //'P' for PCF8523 chip or 'D' for DS3231 chip
#define RTC_CSV_HEADER "Date_Time,"

/* --------------------------------------*/
/* ------ Battery Monitoring -----------*/
/* ------------------------------------*/

#define ENABLE_BATTERY_MONITOR TRUE
#if ENABLE_BATTERY_MONITOR

#define VBATPIN A7                            // A2 on Arduino Weather Shield, A7 on Adafruit Feather Addalogger
#define REFERENCE_V3_PIN NULL                 // A3 on Arduino Weather Shield, A(Doesn't exist?) on Adafruit Feather Addalogger
#define REVERENCE_VOLTAGE_STANDARD 3.3        // The reference voltage is 3.3V on Feathers and the weather shield on UNOs
#define BATT_VOLTAGE_DIVIDER_MULTIPLIER 4.90  // 2 on the Feathers (I think) & 4.90 built into the Weather shield calculated from: (3.9k+1k)/1k
#define MIN_BATT_VOLTS_CUTOFF 5               // voltage at which the batt_voltage_too_low() will return true (and you can make sure to save and shutdown or something...)
#define BATTERY_MONITOR_CSV_HEADER "Battery_Volts,"

#endif

/* -----------------------------------*/
/* ------ SD Card Readers -----------*/
/* ---------------------------------*/

#define DATA_STORAGE_FOLDER_PATH "CTD"  // the folder in the root directory of the sd card to put the files we create (don't include trailing slash)
#define MAX_FILE_SIZE 3900000000        // (in bytes) Technically fat32 supports 4gb files, but I'm putting the cutoff at 3.9 gb.
#define MAIN_SDCARD_CHIP_SELECT_PIN 4   // Addaloger SD Card reader chip select pin is 4, on arduino uno logger shield it's 10.
// #define BACKUP_SDCARD_CHIP_SELECT_PIN 10 // no backup card reader ...yet

/* --------------------------------------------------------*/
/* ------ Electrical Conductivity Sensor Board -----------*/
/* ------------------------------------------------------*/

#define ENABLE_CONDUCTIVITY_SENSOR TRUE
#if ENABLE_CONDUCTIVITY_SENSOR

#include "src/Ezo_I2c_lib/Ezo_i2c.h"
#include "src/SoftwareSerial/SoftwareSerial.h"
#define EC_RX_PIN_NUM 20  //  scl pin on feather m0
#define EC_TX_PIN_NUM 21  //   sda pin on feather m0
#define EC_I2C_ADDR 100   //  (Default: 100) which i2c address the ec board will use when converted to use i2c.
#define CONDUCTIVITY_SENSOR_CSV_HEADER "Conductivity_Microsiemens/cm,"

#endif

/* --------------------------------------*/
/* ------ Temperature Probes -----------*/
/* ------------------------------------*/

#define ENABLE_TEMP_PROBE TRUE
#if ENABLE_TEMP_PROBE

/* This integer specifies how high resolution you want your temperature sensors to be.
   Ok values: 9,10,11,12 (Higher = more accuracy but slower sampling frequency**)
   * ** There is no reason not to use the highest accuracy. This is because the the frequency of the
   conductivity sensor is the limiting factor [min = 1 second] */
#define TEMP_SENSOR_RESOLUTION 12
#define TEMP_SENSOR_DATA_PIN 6
#define NUM_TEMP_PROBES 3
#define TEMP_PROBE_CSV_HEADER "Temp1_C,Temp2_C,Temp3_C,"

#endif
/* -----------------------------------*/
/* ------ Pressure Sensor -----------*/
/* ---------------------------------*/

#define ENABLE_PRESSURE_SENSOR TRUE
#if ENABLE_PRESSURE_SENSOR

/* This integer specifies how high accuracy you want your pressure sensor to be (oversampling resolution).
   Ok values: 256, 512, 1024, 2048, or 4096 (Higher = more accuracy but slower sampling frequency**)
   * ** There is no reason not to use the highest accuracy. This is because the the frequency of the
   conductivity sensor is the limiting factor [min = 1 second] */
#define PRESSURE_SENSOR_RESOLUTION 4096
#define PRESSURE_SENSOR_CSV_HEADER "Pressure_mBar,"

#endif

/* --------------------------------------*/
/* ------ Orientation IMU Sensor -------*/
/* ------------------------------------*/

#define ENABLE_BNO055_ORIENTATION_SENSOR FALSE
#if ENABLE_BNO055_ORIENTATION_SENSOR

#define BNO055_I2C_ADDRESS 0x28  // Check I2C orientation sensor address and correct line (by default address is 0x29 or 0x28)
#define BNO055_CHIP_ID 55
#define BNO055_SAMPLERATE_DELAY_MS (100)  // Set the delay between fresh samples of the orientation sensor (may or may not do anything)
#define DEGREE_TO_RADIAN ((2 * PI) / 360)
#define INCLUDE_CARDINAL_REFERENCE_ORENTATION_FUNCS true
#define BNO055_ORIENTATION_SENSOR_CSV_HEADER "Total_Yaw_Angle_Deg,NS_Lean_Angle_Deg,EW_Lean_Angle_Deg,NS_Acceleration_m/s^2,EW_Acceleration_m/s^2,"

#endif
/* ----------------------------------------------------*/
/* ------ Ambient Light Sensor (BH1750) --------*/
/* --------------------------------------------------*/

#define ENABLE_LIGHT_SENSOR FALSE
#if ENABLE_LIGHT_SENSOR
#define LIGHT_SENSOR_I2C_ADDR 0x23 // 0x23 = 35  | switch jumper to change address to 0x5C
#define LIGHT_SENSOR_CSV_HEADER "Light_Level_Lux,"

#endif

/* ---------------------------------------------*/
/* ---- Calibration / Saved info Config: ------*/
/* -------------------------------------------*/

#define CONFIG_STORAGE_FOLDER_PATH "/ctd/saved_configurations/"

/*
Each of the below structs groups the configuration and/or calibration values for either the components physically attached to the feather board,
like the light_sensor, or components embeded in the ctd tube, like the temperature probes. They are seperate to allow saved calibration of componenents
to be partially restored, even if the featherwing is plugged into a different tube than it was calibrated with.
   When the feather board boots up, it looks for two files, one for each of the below configs.
   The onboard_config is saved to a file named with the feather's serial number to make sure it is only applied to the same feather board if the sd card is wrongly swapped.
   The tube_components_config is saved to a file named with the one of the temperature probe's serial numbers to make sure it is only applied to the same tube that the calibrations were saved for .
*/

typedef struct
{
  bool log_raw_values = false;                     // default value is false - if true it will only log uncalibrated raw values, bypassing calibration
  float seconds_between_log_events = 1.0;  // default value is 1 log row per second (while you can go lower like 0.25, the e conductivity and temp sensors will still only update at their maximum frequecy of ~1 second).
  // If the feather is rebooted it will try to keep writing to the last open log file unless that logfile was last modified more than the following number of seconds ago:
  int max_seconds_to_resume_writing_to_previous_logfile_after_reboot = 60;  // default is 1 minute (60sec)
  char last_datalog_file_path[50] = "";                                     // set to the file path of the datalog file that is currently open, or was open on last boot up. Allows the above mentioned "continue writing" feature.
} onboard_config_type;

// struct tube_components_config_type
// {
//    // Pressure Calibration Values:
//    float pressure_calib_low_measured_value = NAN;
//    float pressure_calib_low_true_value_millipascals = NAN;
//    float pressure_calib_high_measured_value = NAN;
//    float pressure_calib_high_true_value_millipascals = NAN;

//    // Temp Probe Calibration Values:
//    float temp_probe_calib_high_measured_values[NUM_TEMP_PROBES]; // when calibration is run in the (high temp) water bath, the values each temp sensor reports are stored here.
//    float temp_probe_calib_low_measured_values[NUM_TEMP_PROBES];  // when calibration is run in the (low temp) water bath, the values each temp sensor reports are stored here.
//    float temp_probe_calib_high_true_value_c = NAN;                     // when calibration is run in the (high temp) water bath, the true temperature of the bath is stored here in C (we only need one value because we assume the probes all got calibrated in the same bath).
//    float temp_probe_calib_low_true_value_c = NAN;                      // when calibration is run in the (low temp) water bath, the true temperature of the bath is stored here in C (we only ...).
// } tube_components_config;

// Sanity checks to make sure this microcontroller is plugged into the same sensors it has calibrations for, and that the calibration values are correctly formatted.
//  uint8_t saved_config_version_number;    // This must be the first item in the struct and it must be of uint8_t type to work!
//  DeviceAddress known_temp_probe_address; // This stores one of the temp probe's Unique Identifiers, which is used to check that we are plugged into the same ctd tube that the calibrations were performed for!

#endif

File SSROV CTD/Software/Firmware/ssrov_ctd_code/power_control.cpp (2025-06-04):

#include "power_control.hpp"
#include "indicator_light.hpp"

#define POWER_CTRL_SENSE_PIN A5
#define POWER_CTRL_OUTPUT_PIN 11
#define POWER_CTRL_HOLD_ON HIGH
#define POWER_CTRL_HOLD_OFF LOW
#define POWER_CTRL_ONOFF_HOLD_DELAY 1000  //ms
#define POWER_CTRL_ON_THRESHOLD_VOLTAGE 2.0

float power_ctrl_start_voltage = 0;
volatile long unsigned int power_ctrl_hold_start_time = 0;
volatile bool powerup_hold_delay_complete = false;
volatile bool switch_has_been_released_flag = false;
volatile bool isTimerLedOn = false;
volatile bool board_will_power_down = false;

void power_ctrl_setup() {
  indicator_light_on(LED_STAT3);
  pinMode(POWER_CTRL_OUTPUT_PIN, OUTPUT);
  pinMode(POWER_CTRL_SENSE_PIN, INPUT);                     // changed
  digitalWrite(POWER_CTRL_OUTPUT_PIN, POWER_CTRL_HOLD_ON);  // KEEP BOARD ON
  power_ctrl_hold_start_time = millis();
  power_ctrl_start_voltage = power_ctrl_get_switch_voltage();
}

inline float power_ctrl_get_switch_voltage() {
  analogRead(POWER_CTRL_SENSE_PIN);  // Warm-up read - throw away.
  volatile float raw_value = (float)analogRead(POWER_CTRL_SENSE_PIN);
  return 3.33 * raw_value / 1023.0;
}

void power_ctl_show_mag_state(bool flash) {
  if (!flash) {
    indicator_light_off(LED_STAT1);
    indicator_light_off(LED_STAT2);
    indicator_light_off(LED_STAT3);
    return;
  } else {
    indicator_light_on(LED_STAT3);
  }
}

unsigned long lastPowerCheckTime = 0;
void power_ctrl_check_switch() {
  if (millis() < lastPowerCheckTime + 200) return;
  lastPowerCheckTime = millis();

  // Read the state of the magnet switch:
  volatile float switch_voltage = power_ctrl_get_switch_voltage();
  if (switch_voltage > POWER_CTRL_ON_THRESHOLD_VOLTAGE) {
    if (millis() > power_ctrl_hold_start_time + POWER_CTRL_ONOFF_HOLD_DELAY) {
      if (switch_has_been_released_flag) {
        digitalWrite(POWER_CTRL_OUTPUT_PIN, POWER_CTRL_HOLD_OFF);  // TURN OFF BOARD.
        board_will_power_down = true;
        isTimerLedOn = false;
      }
    } else {
      isTimerLedOn = !isTimerLedOn;
    }
    if (!board_will_power_down) indicator_light_on(LED_STAT2);
  } else {
    indicator_light_off(LED_STAT2);
    power_ctrl_hold_start_time = millis();  // KEEP RESETING THE HOLD START TIME WHILE THE POWER SWITCH IS NOT PRESSED.
    switch_has_been_released_flag = true;
    isTimerLedOn = false;
  }
  //power_ctl_show_mag_state(isTimerLedOn);
  if (isTimerLedOn && !board_will_power_down) indicator_light_on(LED_STAT3);
  else indicator_light_off(LED_STAT3);
}



// volatile float sw_voltages[4000] = { 0 };

// float power_ctrl_get_switch_voltage() {
//   // pinMode(POWER_CTRL_SENSE_PIN, INPUT_PULLUP);
//   // pinMode(POWER_CTRL_SENSE_PIN, INPUT_PULLUP);
//   analogRead(POWER_CTRL_SENSE_PIN);  // Warm-up read.
//   float raw_value = (float)analogRead(POWER_CTRL_SENSE_PIN);
//   return 3.33 * raw_value / 1023.0;
// }

// void resetSwitchInterrupts();


// #define SWITCH_ON_THRESHOLD 2.0
// void onPowerSwitchPressed() {
//   detachInterrupt(digitalPinToInterrupt(A5));
//   indicator_light_on(LED_STAT3);
//   delayMicroseconds(10000);           // 10 ms
//   pinMode(POWER_CTRL_SENSE_PIN, INPUT); //CHANGE

//   uint i = 0;
//   float voltage;
//   float lastVoltage = infinityf();
//   bool flipflop = false;
//   analogRead(POWER_CTRL_SENSE_PIN);  // Warm-up read.
//   analogRead(POWER_CTRL_SENSE_PIN);  // Warm-up read.

//   while (i < POWER_CTRL_ONOFF_HOLD_DELAY) {
//     // Flash Light:
//     if (i % 80 == 0) flipflop = !flipflop;
//     if (flipflop) indicator_light_on(LED_STAT3);
//     else indicator_light_off(LED_STAT3);

//     // Wait a bit:
//     delayMicroseconds(1000);           // 1 ms

//     // Check the switch state:
//     analogRead(POWER_CTRL_SENSE_PIN);  // Warm-up read.
//     float raw_value = (float)analogRead(POWER_CTRL_SENSE_PIN);
//     voltage = 3.33 * raw_value / 1023.0;

//     // break out of loop if switch turns off in the middle of waiting:
//     //  && lastVoltage < SWITCH_ON_THRESHOLD
//     if (voltage < SWITCH_ON_THRESHOLD) {
//       indicator_light_off(3);
//       switch_has_been_released_flag = true;
//       attachInterrupt(digitalPinToInterrupt(A5), onPowerSwitchPressed, RISING);
//       return;
//     } else {
//       indicator_light_on(LED_STAT3);
//     }
//     lastVoltage = voltage;
//     // sw_voltages[i] = voltage;
//     // if (voltage < minvoltage) minvoltage = voltage;
//     // if (voltage > maxvoltage) maxvoltage = voltage;
//     i++;
//   }
//   pinMode(POWER_CTRL_SENSE_PIN, INPUT);
//   if (switch_has_been_released_flag) {
//     digitalWrite(POWER_CTRL_OUTPUT_PIN, POWER_CTRL_HOLD_OFF);
//     // indicator_light_off(LED_STAT3);

//   }
//   // } else {
//      attachInterrupt(digitalPinToInterrupt(A5), onPowerSwitchPressed, CHANGE);

//   // print("Power Switch ON=");
//   // print("MS");
//   // Serial.println(millis());
//   // println("minv");
//   // Serial.println(minvoltage);
//   // println("maxv");
//   // Serial.println(maxvoltage);
//   //
//   // interrupts();
// }


// void resetSwitchInterrupts() {
//   detachInterrupt(digitalPinToInterrupt(A5));
//   attachInterrupt(digitalPinToInterrupt(A5), onPowerSwitchPressed, RISING);
// }

// void power_ctrl_setup() {
//   digitalWrite(POWER_CTRL_OUTPUT_PIN, POWER_CTRL_HOLD_ON);  // KEEP BOARD ON
//   // pinMode(A4, OUTPUT);
//   pinMode(POWER_CTRL_OUTPUT_PIN, OUTPUT);
//   pinMode(POWER_CTRL_SENSE_PIN, INPUT); // changed
//   power_ctrl_hold_start_time = millis();
//   // digitalWrite(A4, 1);
//   power_ctrl_start_voltage = power_ctrl_get_switch_voltage();
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

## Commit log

2023-08-08 Add SSROV CTD Hardware
    [2-inch_PVC_PaintCap_Bottom.stl, 22-05-3081.stp, 22-16-2041.stp, 2795 Feather 32u4 Adalogger with pins.step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]
2024-09-09 updated pcb design sept 2024
    [BH1750FVI-TR.stp, Push_button_XKB5858-W-F-75 - Part 1.step, bom.csv, designators.csv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]
2024-09-09 update 3d printing models and guide
    [2-inch_PVC_PaintCap_Bottom.stl, CTD Chassis Part A.3mf, CTD Chassis Part B.3mf, Mag Switch Tool.3mf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]
2024-09-09 organization of ssrov-kicad and documentation updates
    [22-05-3081.stp, 22-16-2041.stp, 2795 Feather 32u4 Adalogger with pins.step, 2795 Feather 32u4 Adalogger.stl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]
2024-09-27 Add tube build guide and organize hardware folder
    [2-inch_PVC_PaintCap_Bottom.stl, CTD Chassis Part A.3mf, CTD Chassis Part B.3mf, Mag Switch Tool.3mf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]
2025-06-04 OpenCTD SSROV PCB Board revision 10
    [bom.csv, designators.csv, positions.csv, ssrov-kicad-openctd.kicad_pcb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]
2025-06-04 clean up kicad pcb file leftovers and readme
    [ssrov-kicad-openctd.kicad_pcb]
